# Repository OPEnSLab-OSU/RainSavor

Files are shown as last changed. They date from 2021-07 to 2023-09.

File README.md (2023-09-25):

# RainSavor
The RainSavor system by the OPEnS Lab measures the electrical conductivity of rainfall. Precipitation is collected in a cup with 2 wires for measuring electrical conductivity at the bottom and two wires for measuring water height at the top. The cup is emptied automatically from the bottom once the water reaches a set height by a siphon. The maximum measurable conductivity value and resolution are set with an I2C AD5246 variable resistor. Temperature and relative humidity are measured with an SHT31 sensor. All data is timestamped and logged to a microSD card at a set time interval with the device on standby between measurements. See the RainSavor wiki for more information: https://github.com/OPEnSLab-OSU/OPEnS-Lab-Home/wiki/RainSavor.

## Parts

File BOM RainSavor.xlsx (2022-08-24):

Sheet: Title Page and Total Cost
RainSavor Bill of Materials
Document updated/edited by: | Cameron Whitlow
Most recent update: | 2021-08-03
Per 1 Smart Rock:
Mechanical Components Total: | $106.55
Electrical Components Total: | $92.84
Labor:
Overall Cost: | $199.39

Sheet: Mechanical Components
Mechanical Components
Cost per device: | $106.55
ID number | Item Description | Quantity Given | Quantity per device | Retail Cost | Cost Per Device | Purchasing quantity | Cost for Required quantity | Product/site info | Notes
 | Davis Rain Funnel | 1 | 1 | $31.95 | $31.95 | 1 |  | Weathershack (https://www.weathershack.com/product/davis-instruments-6462.html)
 | Horizontal T Post | 4 | 1 | $19.29 | $4.82 |  |  | Amazon (https://www.amazon.com/T-Post-Bracket-3-Horizonta-4-Pack/dp/B01NB0FTKH)
 | Vertical T Post | 4 | 1 | $19.29 | $4.82 |  |  | Amazon (https://www.amazon.com/EFL-T-Post-Bracket-Vertical-4-Pack/dp/B01N17VLPI)
 | Pelican Case | 1 | 1 | $14.72 | $14.72 |  |  | BHphotovideo (https://www.bhphotovideo.com/c/product/257871-REG/Pelican_1040_025_120_1040_Micro_Case_Solid.html)
 | Tough Resin | 1 | 1 | $8.00 | $8.00
 | ASA for mount | 1 | 1 | $2.00 | $2.00
 | PG7 Cable Glands | 20 | 2 | $7.99 | $0.80 | 1 |  | Amazon (https://smile.amazon.com/Lokman-Plastic-Waterproof-Adjustable-Connectors/dp/B06Y5HGYK2)
 | Silica Packets |  | 1
 | Screws
 | Hex Nuts
 | T post | 1 | 1 | $3.99 | $3.99 | 1 |  | Tractor Supply (https://www.tractorsupply.com/tsc/product/studded-t-post-5-ft-125-lb-per-foot-3609099)
F221B1/16 BK100 | Heat Shrink | 1 | 1 | $16.00 | $16.00 |  |  | Digikey (https://www.digikey.com/en/products/detail/alpha-wire/F221B1-16-BK100/281667) | For waterproofing solder joint/protecting against shorts
PRT-11375 | Colored Wire | 1 | 1 | $16.95 | $16.95 |  |  | Digikey (https://www.digikey.com/en/products/detail/sparkfun-electronics/PRT-11375/5956252) | This is enough wire to make multiple units, other sources for smaller amounts can be found
744 | Waterproof Connector | 1 | 1 | $2.50 | $2.50 |  |  | Adafruit (https://www.adafruit.com/product/744) | Connection between pelican case and the davis rain funnel
 |  |  |  |  | #DIV/0!
 |  |  |  |  | #DIV/0!
 |  |  |  |  | #DIV/0!
 |  |  |  |  | #DIV/0!
 |  |  |  |  | #DIV/0!
 |  |  |  |  | #DIV/0!
 |  |  |  |  | #DIV/0!
 |  |  |  |  | #DIV/0!
 |  |  |  |  | #DIV/0!
 |  |  |  |  | #DIV/0!
 |  |  |  |  | #DIV/0!
 |  |  |  |  | #DIV/0!
 |  |  |  |  | #DIV/0!
 |  |  |  |  | #DIV/0!
 |  |  |  |  | #DIV/0!
 |  |  |  |  | #DIV/0!
 |  |  |  |  | #DIV/0!
 |  |  |  |  | #DIV/0!
 |  |  |  |  | #DIV/0!
 |  |  |  |  | #DIV/0!
 |  |  |  |  | #DIV/0!
 |  |  |  |  | #DIV/0!
 |  |  |  |  | #DIV/0!
 |  |  |  |  | #DIV/0!
 |  |  |  |  | #DIV/0!
 |  |  |  |  | #DIV/0!
 |  |  |  |  | #DIV/0!
 |  |  |  |  | #DIV/0!
 |  |  |  |  | #DIV/0!
 |  |  |  |  | #DIV/0!
 |  |  |  |  | #DIV/0!
 |  |  |  |  | #DIV/0!
 |  |  |  |  | #DIV/0!
 |  |  |  |  | #DIV/0!
 |  |  |  |  | #DIV/0!
 |  |  |  |  | #DIV/0!
 |  |  |  |  | #DIV/0!
 |  |  |  |  | #DIV/0!
 |  |  |  |  | #DIV/0!
 |  |  |  |  | #DIV/0!
 |  |  |  |  | #DIV/0!
 |  |  |  |  | $0.00
 |  |  |  |  | $0.00
 |  |  |  |  | $0.00
 |  |  |  |  | $0.00
 |  |  |  |  | $0.00
 |  |  |  |  | $0.00
 |  |  |  |  | $0.00
 |  |  |  |  | $0.00
 |  |  |  |  | $0.00
 |  |  |  |  | $0.00
 |  |  |  |  | $0.00
 |  |  |  |  | $0.00
 |  |  |  |  | $0.00
 |  |  |  |  | $0.00
 |  |  |  |  | $0.00
 |  |  |  |  | $0.00
 |  |  |  |  | $0.00
 |  |  |  |  | $0.00
 |  |  |  |  | $0.00
 |  |  |  |  | $0.00
 |  |  |  |  | $0.00
 |  |  |  |  | $0.00
 |  |  |  |  | $0.00
 |  |  |  |  | $0.00
 |  |  |  |  | $0.00
 |  |  |  |  | $0.00
 |  |  |  |  | $0.00
 |  |  |  |  | $0.00
 |  |  |  |  | $0.00
 |  |  |  |  | $0.00
 |  |  |  |  | $0.00
 |  |  |  |  | $0.00
 |  |  |  |  | $0.00
 |  |  |  |  | $0.00
 |  |  |  |  | $0.00
 |  |  |  |  | $0.00
 |  |  |  |  | $0.00
 |  |  |  |  | $0.00
 |  |  |  |  | $0.00
 |  |  |  |  | $0.00
 |  |  |  |  | $0.00
 |  |  |  |  | $0.00
 |  |  |  |  | $0.00
 |  |  |  |  | $0.00
 |  |  |  |  | $0.00
 |  |  |  |  | $0.00
 |  |  |  |  | $0.00
 |  |  |  |  | $0.00
 |  |  |  |  | $0.00
 |  |  |  |  | $0.00
 |  |  |  |  | $0.00
 |  |  |  |  | $0.00
 |  |  |  |  | $0.00
 |  |  |  |  | $0.00
 |  |  |  |  | $0.00
 |  |  |  |  | $0.00
 |  |  |  |  | $0.00
 |  |  |  |  | $0.00
 |  |  |  |  | $0.00
 |  |  |  |  | $0.00
 |  |  |  |  | $0.00
 |  |  |  |  | $0.00
 |  |  |  |  | $0.00
 |  |  |  |  | $0.00
 |  |  |  |  | $0.00
 |  |  |  |  | $0.00
 |  |  |  |  | $0.00
 |  |  |  |  | $0.00
 |  |  |  |  | $0.00
 |  |  |  |  | $0.00
 |  |  |  |  | $0.00
 |  |  |  |  | $0.00
 |  |  |  |  | $0.00
 |  |  |  |  | $0.00
 |  |  |  |  | $0.00
 |  |  |  |  | $0.00
 |  |  |  |  | $0.00
 |  |  |  |  | $0.00
 |  |  |  |  | $0.00
 |  |  |  |  | $0.00
 |  |  |  |  | $0.00
 |  |  |  |  | $0.00
 |  |  |  |  | $0.00
 |  |  |  |  | $0.00
 |  |  |  |  | $0.00
 |  |  |  |  | $0.00
 |  |  |  |  | $0.00
 |  |  |  |  | $0.00
 |  |  |  |  | $0.00
 |  |  |  |  | $0.00
 |  |  |  |  | $0.00
 |  |  |  |  | $0.00
 |  |  |  |  | $0.00
 |  |  |  |  | $0.00
 |  |  |  |  | $0.00
 |  |  |  |  | $0.00
 |  |  |  |  | $0.00
 |  |  |  |  | $0.00
 |  |  |  |  | $0.00
 |  |  |  |  | $0.00
 |  |  |  |  | $0.00
 |  |  |  |  | $0.00
 |  |  |  |  | $0.00
 |  |  |  |  | $0.00
 |  |  |  |  | $0.00
 |  |  |  |  | $0.00
 |  |  |  |  | $0.00
 |  |  |  |  | $0.00
 |  |  |  |  | $0.00
 |  |  |  |  | $0.00
 |  |  |  |  | $0.00
 |  |  |  |  | $0.00
 |  |  |  |  | $0.00
 |  |  |  |  | $0.00
 |  |  |  |  | $0.00
 |  |  |  |  | $0.00
 |  |  |  |  | $0.00
 |  |  |  |  | $0.00
 |  |  |  |  | $0.00
 |  |  |  |  | $0.00
 |  |  |  |  | $0.00
 |  |  |  |  | $0.00
 |  |  |  |  | $0.00
 |  |  |  |  | $0.00
 |  |  |  |  | $0.00
 |  |  |  |  | $0.00
 |  |  |  |  | $0.00
 |  |  |  |  | $0.00
 |  |  |  |  | $0.00
 |  |  |  |  | $0.00
 |  |  |  |  | $0.00
 |  |  |  |  | $0.00
 |  |  |  |  | $0.00
 |  |  |  |  | $0.00
 |  |  |  |  | $0.00
 |  |  |  |  | $0.00
 |  |  |  |  | $0.00
 |  |  |  |  | $0.00
 |  |  |  |  | $0.00
 |  |  |  |  | $0.00
 |  |  |  |  | $0.00
 |  |  |  |  | $0.00
 |  |  |  |  | $0.00
 |  |  |  |  | $0.00
 |  |  |  |  | $0.00
 |  |  |  |  | $0.00
 |  |  |  |  | $0.00
 |  |  |  |  | $0.00
 |  |  |  |  | $0.00
 |  |  |  |  | $0.00
 |  |  |  |  | $0.00
 |  |  |  |  | $0.00
 |  |  |  |  | $0.00
 |  |  |  |  | $0.00
 |  |  |  |  | $0.00
 |  |  |  |  | $0.00
 |  |  |  |  | $0.00
 |  |  |  |  | $0.00
 |  |  |  |  | $0.00
 |  |  |  |  | $0.00
 |  |  |  |  | $0.00
 |  |  |  |  | $0.00
 |  |  |  |  | $0.00
 |  |  |  |  | $0.00
 |  |  |  |  | $0.00
 |  |  |  |  | $0.00
 |  |  |  |  | $0.00
 |  |  |  |  | $0.00
 |  |  |  |  | $0.00
 |  |  |  |  | $0.00
 |  |  |  |  | $0.00
 |  |  |  |  | $0.00
 |  |  |  |  | $0.00
 |  |  |  |  | $0.00
 |  |  |  |  | $0.00
 |  |  |  |  | $0.00
 |  |  |  |  | $0.00
 |  |  |  |  | $0.00
 |  |  |  |  | $0.00
 |  |  |  |  | $0.00
 |  |  |  |  | $0.00
 |  |  |  |  | $0.00
 |  |  |  |  | $0.00
 |  |  |  |  | $0.00
 |  |  |  |  | $0.00
 |  |  |  |  | $0.00
 |  |  |  |  | $0.00
 |  |  |  |  | $0.00
 |  |  |  |  | $0.00
 |  |  |  |  | $0.00
 |  |  |  |  | $0.00
 |  |  |  |  | $0.00
 |  |  |  |  | $0.00
 |  |  |  |  | $0.00
 |  |  |  |  | $0.00
 |  |  |  |  | $0.00
 |  |  |  |  | $0.00
 |  |  |  |  | $0.00
 |  |  |  |  | $0.00
 |  |  |  |  | $0.00
 |  |  |  |  | $0.00
 |  |  |  |  | $0.00
 |  |  |  |  | $0.00
 |  |  |  |  | $0.00
 |  |  |  |  | $0.00
 |  |  |  |  | $0.00
 |  |  |  |  | $0.00
 |  |  |  |  | $0.00
 |  |  |  |  | $0.00
 |  |  |  |  | $0.00
 |  |  |  |  | $0.00
 |  |  |  |  | $0.00
 |  |  |  |  | $0.00
 |  |  |  |  | $0.00
 |  |  |  |  | $0.00
 |  |  |  |  | $0.00
 |  |  |  |  | $0.00
 |  |  |  |  | $0.00
 |  |  |  |  | $0.00
 |  |  |  |  | $0.00
 |  |  |  |  | $0.00
 |  |  |  |  | $0.00
 |  |  |  |  | $0.00
 |  |  |  |  | $0.00
 |  |  |  |  | $0.00
 |  |  |  |  | $0.00
 |  |  |  |  | $0.00
 |  |  |  |  | $0.00
 |  |  |  |  | $0.00
 |  |  |  |  | $0.00
 |  |  |  |  | $0.00
 |  |  |  |  | $0.00
 |  |  |  |  | $0.00
 |  |  |  |  | $0.00
 |  |  |  |  | $0.00
 |  |  |  |  | $0.00
 |  |  |  |  | $0.00
 |  |  |  |  | $0.00
 |  |  |  |  | $0.00
 |  |  |  |  | $0.00
 |  |  |  |  | $0.00
 |  |  |  |  | $0.00
 |  |  |  |  | $0.00
 |  |  |  |  | $0.00
 |  |  |  |  | $0.00
 |  |  |  |  | $0.00
 |  |  |  |  | $0.00
 |  |  |  |  | $0.00
 |  |  |  |  | $0.00
 |  |  |  |  | $0.00
 |  |  |  |  | $0.00
 |  |  |  |  | $0.00
 |  |  |  |  | $0.00
 |  |  |  |  | $0.00
 |  |  |  |  | $0.00
 |  |  |  |  | $0.00
 |  |  |  |  | $0.00
 |  |  |  |  | $0.00
 |  |  |  |  | $0.00
 |  |  |  |  | $0.00
 |  |  |  |  | $0.00
 |  |  |  |  | $0.00
 |  |  |  |  | $0.00
 |  |  |  |  | $0.00
 |  |  |  |  | $0.00
 |  |  |  |  | $0.00
 |  |  |  |  | $0.00
 |  |  |  |  | $0.00
 |  |  |  |  | $0.00
 |  |  |  |  | $0.00
 |  |  |  |  | $0.00
 |  |  |  |  | $0.00
 |  |  |  |  | $0.00
 |  |  |  |  | $0.00
 |  |  |  |  | $0.00
 |  |  |  |  | $0.00
 |  |  |  |  | $0.00
 |  |  |  |  | $0.00
 |  |  |  |  | $0.00
 |  |  |  |  | $0.00
 |  |  |  |  | $0.00
 |  |  |  |  | $0.00
 |  |  |  |  | $0.00
 |  |  |  |  | $0.00
 |  |  |  |  | $0.00
 |  |  |  |  | $0.00
 |  |  |  |  | $0.00
 |  |  |  |  | $0.00
 |  |  |  |  | $0.00
 |  |  |  |  | $0.00
 |  |  |  |  | $0.00
 |  |  |  |  | $0.00
 |  |  |  |  | $0.00
 |  |  |  |  | $0.00
 |  |  |  |  | $0.00
 |  |  |  |  | $0.00
 |  |  |  |  | $0.00
 |  |  |  |  | $0.00
 |  |  |  |  | $0.00
 |  |  |  |  | $0.00
 |  |  |  |  | $0.00
 |  |  |  |  | $0.00
 |  |  |  |  | $0.00
 |  |  |  |  | $0.00
 |  |  |  |  | $0.00
 |  |  |  |  | $0.00
 |  |  |  |  | $0.00
 |  |  |  |  | $0.00
 |  |  |  |  | $0.00
 |  |  |  |  | $0.00
 |  |  |  |  | $0.00
 |  |  |  |  | $0.00
 |  |  |  |  | $0.00
 |  |  |  |  | $0.00
 |  |  |  |  | $0.00
 |  |  |  |  | $0.00
 |  |  |  |  | $0.00
 |  |  |  |  | $0.00
 |  |  |  |  | $0.00
 |  |  |  |  | $0.00
 |  |  |  |  | $0.00
 |  |  |  |  | $0.00
 |  |  |  |  | $0.00
 |  |  |  |  | $0.00
 |  |  |  |  | $0.00
 |  |  |  |  | $0.00
 |  |  |  |  | $0.00
 |  |  |  |  | $0.00
 |  |  |  |  | $0.00
 |  |  |  |  | $0.00
 |  |  |  |  | $0.00
 |  |  |  |  | $0.00
 |  |  |  |  | $0.00
 |  |  |  |  | $0.00
 |  |  |  |  | $0.00
 |  |  |  |  | $0.00
 |  |  |  |  | $0.00
 |  |  |  |  | $0.00
 |  |  |  |  | $0.00
 |  |  |  |  | $0.00
 |  |  |  |  | $0.00
 |  |  |  |  | $0.00
 |  |  |  |  | $0.00
 |  |  |  |  | $0.00
 |  |  |  |  | $0.00
 |  |  |  |  | $0.00
 |  |  |  |  | $0.00
 |  |  |  |  | $0.00
 |  |  |  |  | $0.00
 |  |  |  |  | $0.00
 |  |  |  |  | $0.00
 |  |  |  |  | $0.00
 |  |  |  |  | $0.00
 |  |  |  |  | $0.00
 |  |  |  |  | $0.00
 |  |  |  |  | $0.00
 |  |  |  |  | $0.00
 |  |  |  |  | $0.00
 |  |  |  |  | $0.00
 |  |  |  |  | $0.00
 |  |  |  |  | $0.00
 |  |  |  |  | $0.00
 |  |  |  |  | $0.00
 |  |  |  |  | $0.00
 |  |  |  |  | $0.00
 |  |  |  |  | $0.00
 |  |  |  |  | $0.00
 |  |  |  |  | $0.00
 |  |  |  |  | $0.00
 |  |  |  |  | $0.00
 |  |  |  |  | $0.00
 |  |  |  |  | $0.00
 |  |  |  |  | $0.00
 |  |  |  |  | $0.00
 |  |  |  |  | $0.00
 |  |  |  |  | $0.00
 |  |  |  |  | $0.00
 |  |  |  |  | $0.00
 |  |  |  |  | $0.00
 |  |  |  |  | $0.00
 |  |  |  |  | $0.00
 |  |  |  |  | $0.00
 |  |  |  |  | $0.00
 |  |  |  |  | $0.00
 |  |  |  |  | $0.00
 |  |  |  |  | $0.00
 |  |  |  |  | $0.00
 |  |  |  |  | $0.00
 |  |  |  |  | $0.00
 |  |  |  |  | $0.00
 |  |  |  |  | $0.00
 |  |  |  |  | $0.00
 |  |  |  |  | $0.00
 |  |  |  |  | $0.00
 |  |  |  |  | $0.00
 |  |  |  |  | $0.00
 |  |  |  |  | $0.00
 |  |  |  |  | $0.00
 |  |  |  |  | $0.00
 |  |  |  |  | $0.00
 |  |  |  |  | $0.00
 |  |  |  |  | $0.00
 |  |  |  |  | $0.00
 |  |  |  |  | $0.00
 |  |  |  |  | $0.00
 |  |  |  |  | $0.00
 |  |  |  |  | $0.00
 |  |  |  |  | $0.00
 |  |  |  |  | $0.00
 |  |  |  |  | $0.00
 |  |  |  |  | $0.00
 |  |  |  |  | $0.00
 |  |  |  |  | $0.00
 |  |  |  |  | $0.00
 |  |  |  |  | $0.00
 |  |  |  |  | $0.00
 |  |  |  |  | $0.00
 |  |  |  |  | $0.00
 |  |  |  |  | $0.00
 |  |  |  |  | $0.00
 |  |  |  |  | $0.00
 |  |  |  |  | $0.00
 |  |  |  |  | $0.00
 |  |  |  |  | $0.00
 |  |  |  |  | $0.00
 |  |  |  |  | $0.00
 |  |  |  |  | $0.00
 |  |  |  |  | $0.00
 |  |  |  |  | $0.00
 |  |  |  |  | $0.00
 |  |  |  |  | $0.00
 |  |  |  |  | $0.00
 |  |  |  |  | $0.00
 |  |  |  |  | $0.00
 |  |  |  |  | $0.00
 |  |  |  |  | $0.00
 |  |  |  |  | $0.00
 |  |  |  |  | $0.00
 |  |  |  |  | $0.00
 |  |  |  |  | $0.00
 |  |  |  |  | $0.00
 |  |  |  |  | $0.00
 |  |  |  |  | $0.00
 |  |  |  |  | $0.00
 |  |  |  |  | $0.00
 |  |  |  |  | $0.00
 |  |  |  |  | $0.00
 |  |  |  |  | $0.00
 |  |  |  |  | $0.00
 |  |  |  |  | $0.00
 |  |  |  |  | $0.00
 |  |  |  |  | $0.00
 |  |  |  |  | $0.00
 |  |  |  |  | $0.00
 |  |  |  |  | $0.00
 |  |  |  |  | $0.00
 |  |  |  |  | $0.00
 |  |  |  |  | $0.00
 |  |  |  |  | $0.00
 |  |  |  |  | $0.00
 |  |  |  |  | $0.00
 |  |  |  |  | $0.00
 |  |  |  |  | $0.00
 |  |  |  |  | $0.00
 |  |  |  |  | $0.00
 |  |  |  |  | $0.00
 |  |  |  |  | $0.00
 |  |  |  |  | $0.00
 |  |  |  |  | $0.00
 |  |  |  |  | $0.00
 |  |  |  |  | $0.00
 |  |  |  |  | $0.00
 |  |  |  |  | $0.00
 |  |  |  |  | $0.00
 |  |  |  |  | $0.00
 |  |  |  |  | $0.00
 |  |  |  |  | $0.00
 |  |  |  |  | $0.00
 |  |  |  |  | $0.00
 |  |  |  |  | $0.00
 |  |  |  |  | $0.00
 |  |  |  |  | $0.00
 |  |  |  |  | $0.00
 |  |  |  |  | $0.00
 |  |  |  |  | $0.00
 |  |  |  |  | $0.00
 |  |  |  |  | $0.00
 |  |  |  |  | $0.00
 |  |  |  |  | $0.00
 |  |  |  |  | $0.00
 |  |  |  |  | $0.00
 |  |  |  |  | $0.00
 |  |  |  |  | $0.00
 |  |  |  |  | $0.00
 |  |  |  |  | $0.00
 |  |  |  |  | $0.00
 |  |  |  |  | $0.00
 |  |  |  |  | $0.00
 |  |  |  |  | $0.00
 |  |  |  |  | $0.00
 |  |  |  |  | $0.00
 |  |  |  |  | $0.00
 |  |  |  |  | $0.00
 |  |  |  |  | $0.00
 |  |  |  |  | $0.00
 |  |  |  |  | $0.00
 |  |  |  |  | $0.00
 |  |  |  |  | $0.00
 |  |  |  |  | $0.00
 |  |  |  |  | $0.00
 |  |  |  |  | $0.00
 |  |  |  |  | $0.00
 |  |  |  |  | $0.00
 |  |  |  |  | $0.00
 |  |  |  |  | $0.00
 |  |  |  |  | $0.00
 |  |  |  |  | $0.00
 |  |  |  |  | $0.00
 |  |  |  |  | $0.00
 |  |  |  |  | $0.00
 |  |  |  |  | $0.00
 |  |  |  |  | $0.00
 |  |  |  |  | $0.00
 |  |  |  |  | $0.00
 |  |  |  |  | $0.00
 |  |  |  |  | $0.00
 |  |  |  |  | $0.00
 |  |  |  |  | $0.00
 |  |  |  |  | $0.00
 |  |  |  |  | $0.00
 |  |  |  |  | $0.00
 |  |  |  |  | $0.00
 |  |  |  |  | $0.00
 |  |  |  |  | $0.00
 |  |  |  |  | $0.00
 |  |  |  |  | $0.00
 |  |  |  |  | $0.00
 |  |  |  |  | $0.00
 |  |  |  |  | $0.00
 |  |  |  |  | $0.00
 |  |  |  |  | $0.00
 |  |  |  |  | $0.00
 |  |  |  |  | $0.00
 |  |  |  |  | $0.00
 |  |  |  |  | $0.00
 |  |  |  |  | $0.00
 |  |  |  |  | $0.00
 |  |  |  |  | $0.00
 |  |  |  |  | $0.00
 |  |  |  |  | $0.00
 |  |  |  |  | $0.00
 |  |  |  |  | $0.00
 |  |  |  |  | $0.00
 |  |  |  |  | $0.00
 |  |  |  |  | $0.00
 |  |  |  |  | $0.00
 |  |  |  |  | $0.00
 |  |  |  |  | $0.00
 |  |  |  |  | $0.00
 |  |  |  |  | $0.00
 |  |  |  |  | $0.00
 |  |  |  |  | $0.00
 |  |  |  |  | $0.00
 |  |  |  |  | $0.00
 |  |  |  |  | $0.00
 |  |  |  |  | $0.00
 |  |  |  |  | $0.00
 |  |  |  |  | $0.00
 |  |  |  |  | $0.00
 |  |  |  |  | $0.00
 |  |  |  |  | $0.00
 |  |  |  |  | $0.00
 |  |  |  |  | $0.00
 |  |  |  |  | $0.00
 |  |  |  |  | $0.00
 |  |  |  |  | $0.00
 |  |  |  |  | $0.00
 |  |  |  |  | $0.00
 |  |  |  |  | $0.00
 |  |  |  |  | $0.00
 |  |  |  |  | $0.00
 |  |  |  |  | $0.00
 |  |  |  |  | $0.00
 |  |  |  |  | $0.00
 |  |  |  |  | $0.00
 |  |  |  |  | $0.00
 |  |  |  |  | $0.00
 |  |  |  |  | $0.00
 |  |  |  |  | $0.00
 |  |  |  |  | $0.00
 |  |  |  |  | $0.00
 |  |  |  |  | $0.00
 |  |  |  |  | $0.00
 |  |  |  |  | $0.00
 |  |  |  |  | $0.00
 |  |  |  |  | $0.00
 |  |  |  |  | $0.00
 |  |  |  |  | $0.00
 |  |  |  |  | $0.00
 |  |  |  |  | $0.00
 |  |  |  |  | $0.00
 |  |  |  |  | $0.00
 |  |  |  |  | $0.00
 |  |  |  |  | $0.00
 |  |  |  |  | $0.00
 |  |  |  |  | $0.00
 |  |  |  |  | $0.00
 |  |  |  |  | $0.00
 |  |  |  |  | $0.00
 |  |  |  |  | $0.00
 |  |  |  |  | $0.00
 |  |  |  |  | $0.00
 |  |  |  |  | $0.00
 |  |  |  |  | $0.00
 |  |  |  |  | $0.00
 |  |  |  |  | $0.00
 |  |  |  |  | $0.00
 |  |  |  |  | $0.00
 |  |  |  |  | $0.00
 |  |  |  |  | $0.00
 |  |  |  |  | $0.00
 |  |  |  |  | $0.00
 |  |  |  |  | $0.00
 |  |  |  |  | $0.00
 |  |  |  |  | $0.00
 |  |  |  |  | $0.00
 |  |  |  |  | $0.00
 |  |  |  |  | $0.00
 |  |  |  |  | $0.00
 |  |  |  |  | $0.00
 |  |  |  |  | $0.00
 |  |  |  |  | $0.00
 |  |  |  |  | $0.00
 |  |  |  |  | $0.00
 |  |  |  |  | $0.00
 |  |  |  |  | $0.00
 |  |  |  |  | $0.00
 |  |  |  |  | $0.00
 |  |  |  |  | $0.00
 |  |  |  |  | $0.00
 |  |  |  |  | $0.00
 |  |  |  |  | $0.00
 |  |  |  |  | $0.00
 |  |  |  |  | $0.00
 |  |  |  |  | $0.00
 |  |  |  |  | $0.00
 |  |  |  |  | $0.00
 |  |  |  |  | $0.00
 |  |  |  |  | $0.00
 |  |  |  |  | $0.00
 |  |  |  |  | $0.00
 |  |  |  |  | $0.00
 |  |  |  |  | $0.00
 |  |  |  |  | $0.00
 |  |  |  |  | $0.00
 |  |  |  |  | $0.00
 |  |  |  |  | $0.00
 |  |  |  |  | $0.00
 |  |  |  |  | $0.00
 |  |  |  |  | $0.00
 |  |  |  |  | $0.00
 |  |  |  |  | $0.00
 |  |  |  |  | $0.00
 |  |  |  |  | $0.00
 |  |  |  |  | $0.00
 |  |  |  |  | $0.00
 |  |  |  |  | $0.00
 |  |  |  |  | $0.00
 |  |  |  |  | $0.00
 |  |  |  |  | $0.00
 |  |  |  |  | $0.00
 |  |  |  |  | $0.00
 |  |  |  |  | $0.00
 |  |  |  |  | $0.00
 |  |  |  |  | $0.00
 |  |  |  |  | $0.00
 |  |  |  |  | $0.00
 |  |  |  |  | $0.00
 |  |  |  |  | $0.00
 |  |  |  |  | $0.00
 |  |  |  |  | $0.00
 |  |  |  |  | $0.00
 |  |  |  |  | $0.00
 |  |  |  |  | $0.00
 |  |  |  |  | $0.00
 |  |  |  |  | $0.00
 |  |  |  |  | $0.00
 |  |  |  |  | $0.00
 |  |  |  |  | $0.00
 |  |  |  |  | $0.00
 |  |  |  |  | $0.00
 |  |  |  |  | $0.00
 |  |  |  |  | $0.00
 |  |  |  |  | $0.00
 |  |  |  |  | $0.00
 |  |  |  |  | $0.00
 |  |  |  |  | $0.00
 |  |  |  |  | $0.00
 |  |  |  |  | $0.00
 |  |  |  |  | $0.00
 |  |  |  |  | $0.00
 |  |  |  |  | $0.00
 |  |  |  |  | $0.00
 |  |  |  |  | $0.00
 |  |  |  |  | $0.00
 |  |  |  |  | $0.00
 |  |  |  |  | $0.00
 |  |  |  |  | $0.00
 |  |  |  |  | $0.00
 |  |  |  |  | $0.00
 |  |  |  |  | $0.00
 |  |  |  |  | $0.00
 |  |  |  |  | $0.00
 |  |  |  |  | $0.00
 |  |  |  |  | $0.00
 |  |  |  |  | $0.00
 |  |  |  |  | $0.00
 |  |  |  |  | $0.00
 |  |  |  |  | $0.00
 |  |  |  |  | $0.00
 |  |  |  |  | $0.00
 |  |  |  |  | $0.00
 |  |  |  |  | $0.00
 |  |  |  |  | $0.00
 |  |  |  |  | $0.00
 |  |  |  |  | $0.00
 |  |  |  |  | $0.00
 |  |  |  |  | $0.00
 |  |  |  |  | $0.00
 |  |  |  |  | $0.00
 |  |  |  |  | $0.00
 |  |  |  |  | $0.00
 |  |  |  |  | $0.00
 |  |  |  |  | $0.00
 |  |  |  |  | $0.00
 |  |  |  |  | $0.00
 |  |  |  |  | $0.00
 |  |  |  |  | $0.00
 |  |  |  |  | $0.00
 |  |  |  |  | $0.00
 |  |  |  |  | $0.00
 |  |  |  |  | $0.00
 |  |  |  |  | $0.00
 |  |  |  |  | $0.00
 |  |  |  |  | $0.00
 |  |  |  |  | $0.00
 |  |  |  |  | $0.00
 |  |  |  |  | $0.00
 |  |  |  |  | $0.00
 |  |  |  |  | $0.00
 |  |  |  |  | $0.00
 |  |  |  |  | $0.00
 |  |  |  |  | $0.00
 |  |  |  |  | $0.00
 |  |  |  |  | $0.00
 |  |  |  |  | $0.00
 |  |  |  |  | $0.00
 |  |  |  |  | $0.00
 |  |  |  |  | $0.00
 |  |  |  |  | $0.00
 |  |  |  |  | $0.00
 |  |  |  |  | $0.00
 |  |  |  |  | $0.00
 |  |  |  |  | $0.00
 |  |  |  |  | $0.00
 |  |  |  |  | $0.00
 |  |  |  |  | $0.00
 |  |  |  |  | $0.00
 |  |  |  |  | $0.00
 |  |  |  |  | $0.00
 |  |  |  |  | $0.00
 |  |  |  |  | $0.00
 |  |  |  |  | $0.00
 |  |  |  |  | $0.00
 |  |  |  |  | $0.00
 |  |  |  |  | $0.00
 |  |  |  |  | $0.00
 |  |  |  |  | $0.00
 |  |  |  |  | $0.00
 |  |  |  |  | $0.00
 |  |  |  |  | $0.00
 |  |  |  |  | $0.00
 |  |  |  |  | $0.00
 |  |  |  |  | $0.00
 |  |  |  |  | $0.00
 |  |  |  |  | $0.00
 |  |  |  |  | $0.00
 |  |  |  |  | $0.00
 |  |  |  |  | $0.00
 |  |  |  |  | $0.00
 |  |  |  |  | $0.00
 |  |  |  |  | $0.00
 |  |  |  |  | $0.00
 |  |  |  |  | $0.00
 |  |  |  |  | $0.00
 |  |  |  |  | $0.00
 |  |  |  |  | $0.00
 |  |  |  |  | $0.00
 |  |  |  |  | $0.00
 |  |  |  |  | $0.00
 |  |  |  |  | $0.00
 |  |  |  |  | $0.00
 |  |  |  |  | $0.00
 |  |  |  |  | $0.00
 |  |  |  |  | $0.00
 |  |  |  |  | $0.00
 |  |  |  |  | $0.00
 |  |  |  |  | $0.00
 |  |  |  |  | $0.00
 |  |  |  |  | $0.00
 |  |  |  |  | $0.00
 |  |  |  |  | $0.00
 |  |  |  |  | $0.00
 |  |  |  |  | $0.00
 |  |  |  |  | $0.00
 |  |  |  |  | $0.00
 |  |  |  |  | $0.00
 |  |  |  |  | $0.00
 |  |  |  |  | $0.00
 |  |  |  |  | $0.00
 |  |  |  |  | $0.00
 |  |  |  |  | $0.00
 |  |  |  |  | $0.00
 |  |  |  |  | $0.00
 |  |  |  |  | $0.00
 |  |  |  |  | $0.00
 |  |  |  |  | $0.00
 |  |  |  |  | $0.00
 |  |  |  |  | $0.00
 |  |  |  |  | $0.00
 |  |  |  |  | $0.00
 |  |  |  |  | $0.00
 |  |  |  |  | $0.00
 |  |  |  |  | $0.00
 |  |  |  |  | $0.00
 |  |  |  |  | $0.00
 |  |  |  |  | $0.00
 |  |  |  |  | $0.00
 |  |  |  |  | $0.00
 |  |  |  |  | $0.00
 |  |  |  |  | $0.00
 |  |  |  |  | $0.00
 |  |  |  |  | $0.00
 |  |  |  |  | $0.00
 |  |  |  |  | $0.00
 |  |  |  |  | $0.00
 |  |  |  |  | $0.00
 |  |  |  |  | $0.00
 |  |  |  |  | $0.00
 |  |  |  |  | $0.00
 |  |  |  |  | $0.00
 |  |  |  |  | $0.00
 |  |  |  |  | $0.00
 |  |  |  |  | $0.00
 |  |  |  |  | $0.00
 |  |  |  |  | $0.00
 |  |  |  |  | $0.00
 |  |  |  |  | $0.00
 |  |  |  |  | $0.00
 |  |  |  |  | $0.00
 |  |  |  |  | $0.00
 |  |  |  |  | $0.00
 |  |  |  |  | $0.00
 |  |  |  |  | $0.00
 |  |  |  |  | $0.00
 |  |  |  |  | $0.00
 |  |  |  |  | $0.00
 |  |  |  |  | $0.00
 |  |  |  |  | $0.00
 |  |  |  |  | $0.00
 |  |  |  |  | $0.00
 |  |  |  |  | $0.00
 |  |  |  |  | $0.00
 |  |  |  |  | $0.00
 |  |  |  |  | $0.00
 |  |  |  |  | $0.00
 |  |  |  |  | $0.00
 |  |  |  |  | $0.00
 |  |  |  |  | $0.00
 |  |  |  |  | $0.00
 |  |  |  |  | $0.00
 |  |  |  |  | $0.00
 |  |  |  |  | $0.00
 |  |  |  |  | $0.00
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

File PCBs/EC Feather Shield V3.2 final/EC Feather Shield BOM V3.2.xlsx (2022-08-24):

Item # | Comp # | Qty | Manufacturer | Mfg Part # | Description/Value | Package, Case | Type | Cost per Part | Total Cost
1 | U1 | 1 | Digikey (https://www.digikey.com/en/products/detail/texas-instruments/ADS1115IDGST/2123298) | 296-24934-1-ND | IC ADC 16BIT SIGMA-DELTA 10VSSOP | 10-TFSOP, 10-MSOP (0.118", 3.00mm Width) | Surface Mount | $6.10 | $6.10
2 | U2 | 1 | Digikey (https://www.digikey.com/en/products/detail/texas-instruments/TPS60400DBVR/1672052) | 296-27004-1-ND | IC REG CHARG PUMP INV 60MA SOT23 | SOT-23-5 | Surface Mount | $0.93 | $0.93
3 | U3 | 1 | Digikey (https://www.digikey.com/en/products/detail/texas-instruments/TL074CN/277423) | 296-1777-ND | IC OPAMP JFET 4 CIRCUIT 14DIP | 14-DIP | Through Hole | $0.65 | $0.65
4 | U4 | 1 | Digikey (https://www.digikey.com/en/products/detail/analog-devices-inc/AD5246BKSZ10-RL7/995693) | AD5246BKSZ10-RL7CT-ND | IC DGTL POT 10KOHM 128TAP SC70-6 | 6-TSSOP, SC-88, SOT-363 | Surface Mount | $1.52 | $1.52
5 | C1, C2, C3 | 3 | Digikey (https://www.digikey.com/en/products/detail/kemet/C1206C104KARACTU/992199) | 399-4674-1-ND | CAP CER 0.1UF 250V X7R 1206 | 1206 (3216 Metric) | Surface Mount | $0.35 | $1.05
6 | C4, C5, C6, C7, C8, C9, C10 | 7 | Digikey (https://www.digikey.com/en/products/detail/samsung-electro-mechanics/CL31B105KBHNFNE/3888749) | 1276-3091-1-ND | CAP CER 1UF 50V X7R 1206 | 1206 (3216 Metric) | Surface Mount | $0.15 | $1.05
7 | R1, R4, R6 | 3 | Digikey (https://www.digikey.com/en/products/detail/yageo/RC1206FR-071KL/728387) | 311-1.00KFRCT-ND | RES SMD 1K OHM 1% 1/4W 1206 | 1206 (3216 Metric) | Surface Mount | $0.10 | $0.30
8 | R5 | 1 | Digikey (https://www.digikey.com/en/products/detail/yageo/RC1206JR-072KL/732183) | 311-2.0KERCT-ND | RES SMD 2K OHM 5% 1/4W 1206 | 1206 (3216 Metric) | Surface Mount | $0.10 | $0.10
9 | R8, R11 | 2 | Digikey (https://www.digikey.com/en/products/detail/yageo/RC1206FR-074K7L/731834) | 311-4.70KFRCT-ND | RES SMD 4.7K OHM 1% 1/4W 1206 | 1206 (3216 Metric) | Surface Mount | $0.10 | $0.20
10 | R10 | 1 | Digikey (https://www.digikey.com/en/products/detail/yageo/RT1206BRD075KL/5936961) | YAG5090CT-ND | RES SMD 5K OHM 0.1% 1/4W 1206 | 1206 (3216 Metric) | Surface Mount | $0.63 | $0.63
11 | R2, R7, R9, R12, R13, R14, R15,R17,R18,R19 | 10 | Digikey (https://www.digikey.com/en/products/detail/yageo/RC1206JR-0710KL/732156) | 311-10KERCT-ND | RES SMD 10K OHM 5% 1/4W 1206 | 1206 (3216 Metric) | Surface Mount | $0.10 | $1.00
12 | R3 | 1 | Digikey (https://www.digikey.com/en/products/detail/yageo/RC1206JR-0722KL/732201) | 311-22KERCT-ND | RES SMD 22K OHM 5% 1/4W 1206 | 1206 (3216 Metric) | Surface Mount | $0.10 | $0.10
13 | D1, D2, D3, D4, D5 | 5 | Digikey (https://www.digikey.com/en/products/detail/comchip-technology/1N4001-G/1979675) | 641-1310-1-ND | DIODE GEN PURP 50V 1A DO41 | DO-204AL, DO-41, Axial | Through Hole | $0.10 | $0.50
14 | REED | 1 | Digikey (https://www.digikey.com/en/products/detail/e-switch/EG1218/101726) | EG1903-ND | SWITCH SLIDE SPDT 200MA 30V |  | Through Hole | $0.65 | $0.65
15 | CN1, CN4 | 2 | Digikey (https://www.digikey.com/en/products/detail/jst-sales-america-inc/B2B-PH-K-S(LF)(SN)/926611) | 455-1704-ND | CONN HEADER VERT 2POS 2MM |  | Through Hole | $0.17 | $0.34
16 | JP2 & JP3 (combo) | 1 | Digikey (https://www.digikey.com/en/products/detail/sullins-connector-solutions/PPTC161LFBN-RC/810154) | S7014-ND | CONN HDR 16POS 0.1 TIN PCB |  | Through Hole | $0.98 | $0.98
17 | JP1 | 1 | Digikey (https://www.digikey.com/en/products/detail/sullins-connector-solutions/PPTC121LFBN-RC/807231) | S6100-ND | CONN HDR 12POS 0.1 TIN PCB |  | Through Hole | $0.78 | $0.78
18 | JP5 | 1 | Digikey (https://www.digikey.com/en/products/detail/w%C3%BCrth-elektronik/61300311121/4846825) | 732-5316-ND | CONN HEADER VERT 3POS 2.54MM |  | Through Hole | $0.13 | $0.13
19 | PCB | 1 | OSHPark |  | PCB Print - 3 |  |  | $14.95 | $14.95 | Can also source PCB & Stencil through PCBWay
20 | PCB Stencil | 1 | OSHStencil |  | PCB Stencil |  |  | $22.22 | $22.22
21 | LED1, LED2, LED3 | 3 | Digikey (https://www.digikey.com/en/products/detail/kingbright/APTR3216SGC/1747570) | 754-1171-1-ND | LED GREEN CLEAR SMD BOTTOM ENTRY | 1206 (3216 Metric) | Surface Mount | $0.32 | $0.96
22 | JP4 | 1 | Digikey (https://www.digikey.com/en/products/detail/sullins-connector-solutions/PPPC091LFBN-RC/810181) | S7042-ND | CONN HDR 9POS 0.1 GOLD PCB |  | Through Hole | $0.67 | $0.67
23 | CN2 | 1 | Digikey (https://www.digikey.com/en/products/detail/jst-sales-america-inc/B3B-PH-K-S-LF-SN/926612) | 455-1705-ND | CONN HEADER VERT 3POS 2MM |  | Through Hole | $0.19 | $0.19
24 | CN3 | 1 | Digikey (https://www.digikey.com/en/products/detail/jst-sales-america-inc/B4B-PH-K-S-LF-SN/926613) | 455-1706-ND | CONN HEADER VERT 4POS 2MM |  | Through Hole | $0.24 | $0.24
25 | CN1-F, CN4-F | 2 | Digikey (https://www.digikey.com/en/products/detail/jst-sales-america-inc/PHR-2/608607?ColumnSort=0&FV=-8%7C319&page=1&pageSize=500&sf=0&sv=0) | 455-1165-ND | CONN HOUSING PH 2POS 2MM WHITE |  | Through Hole | $0.10 | $0.20
26 | CN2-F | 1 | Digikey (https://www.digikey.com/en/products/detail/jst-sales-america-inc/PHR-3/527357?ColumnSort=0&FV=-8%7C319&page=1&pageSize=500&sf=0&sv=0) | 455-1126-ND | CONN HOUSING PH 3POS 2.0MM |  | Through Hole | $0.10 | $0.10
27 | CN3-F | 1 | Digikey (https://www.digikey.com/en/products/detail/jst-sales-america-inc/PHR-4/608606?ColumnSort=0&FV=-8%7C319&page=1&pageSize=500&sf=0&sv=0) | 455-1164-ND | CONN HOUSING PH 4POS 2MM WHITE |  | Through Hole | $0.10 | $0.10
 |  |  |  |  |  |  | TOTAL | $51.80 | $55.81
 | Alternatives for U4
1 | U4-2 | 1 | Digikey (https://www.digikey.com/en/products/detail/analog-devices-inc/AD5246BKSZ50-RL7/995689) | AD5246BKSZ50-RL7CT-ND | IC DGTL POT 50KOHM 128TAP SC70-6 | 6-TSSOP, SC-88, SOT-363 | Surface Mount | $1.52
2 | U4-3 | 1 | Digikey (https://www.digikey.com/en/products/detail/analog-devices-inc/AD5246BKSZ100-RL7/750896) | AD5246BKSZ100RLCT-ND | IC DGT POT 100KOHM 128TAP SC70-6 | 6-TSSOP, SC-88, SOT-363 | Surface Mount | $1.52

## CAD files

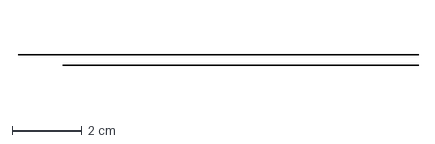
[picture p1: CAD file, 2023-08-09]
CAD/3L_bag_holder.dxf
11.5 x 0.3 cm

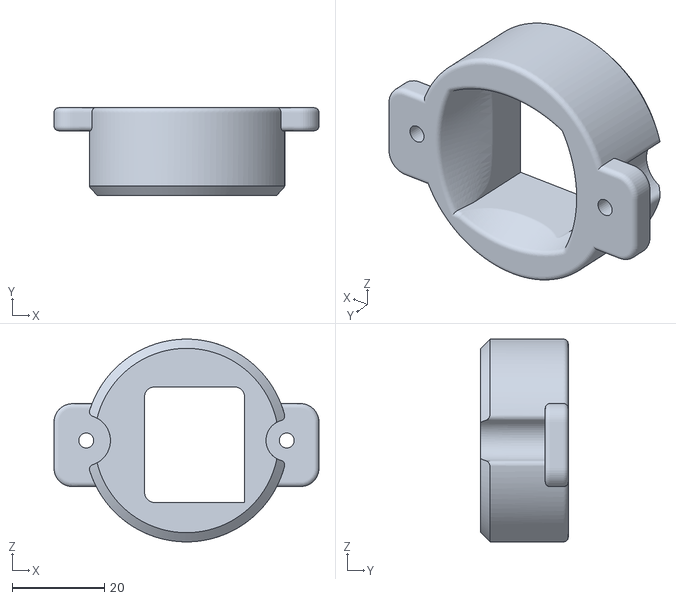
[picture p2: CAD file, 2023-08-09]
CAD/RainSavor_Sleeve.stl
57.5 x 19.0 x 44.0

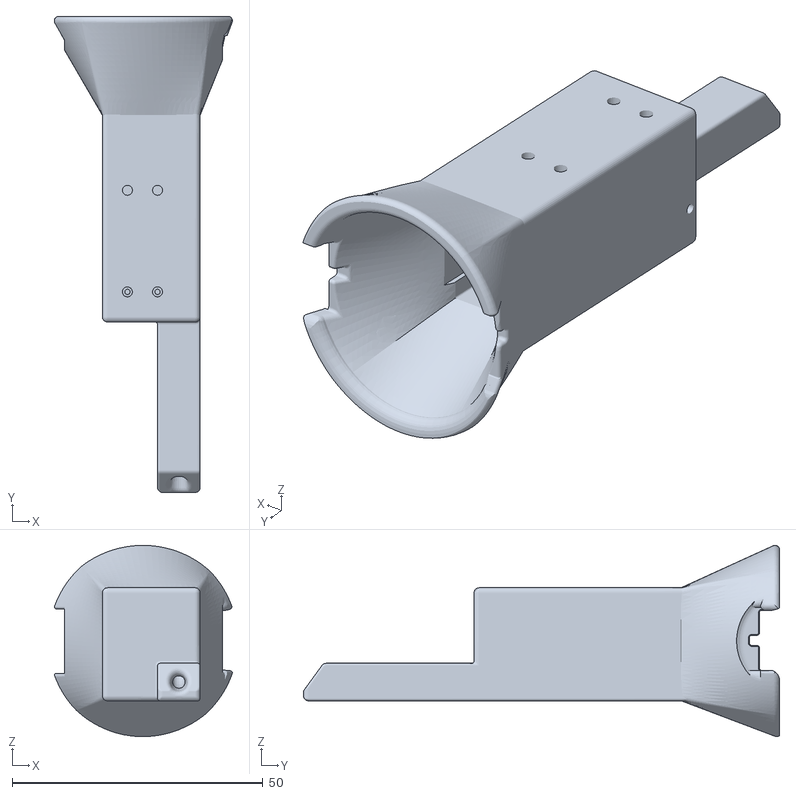
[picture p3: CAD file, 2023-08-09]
CAD/RainSavor_Cup_Funnel.stl
35.6 x 94.9 x 38.1

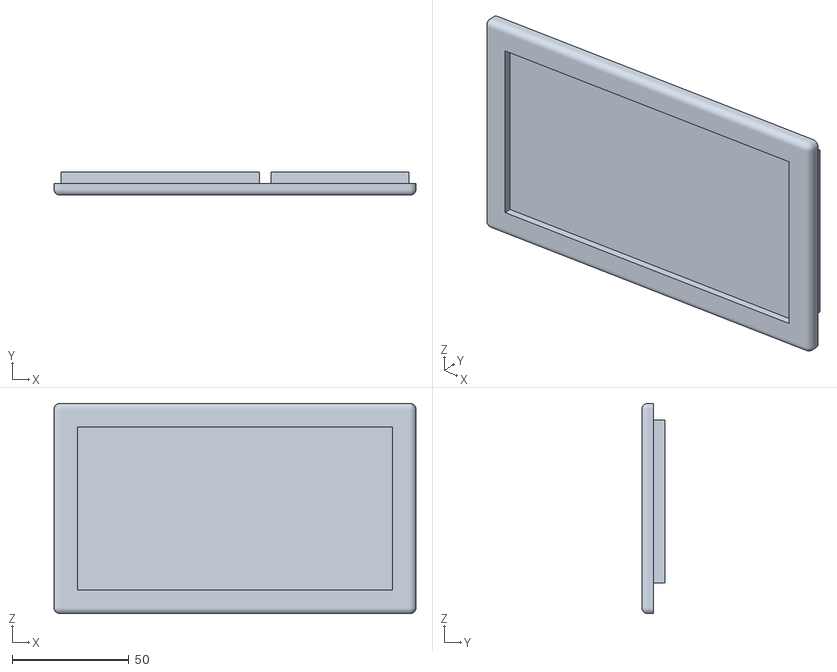
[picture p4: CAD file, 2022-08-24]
CAD/PCB_battery_mount.stl
155.0 x 10.0 x 90.0

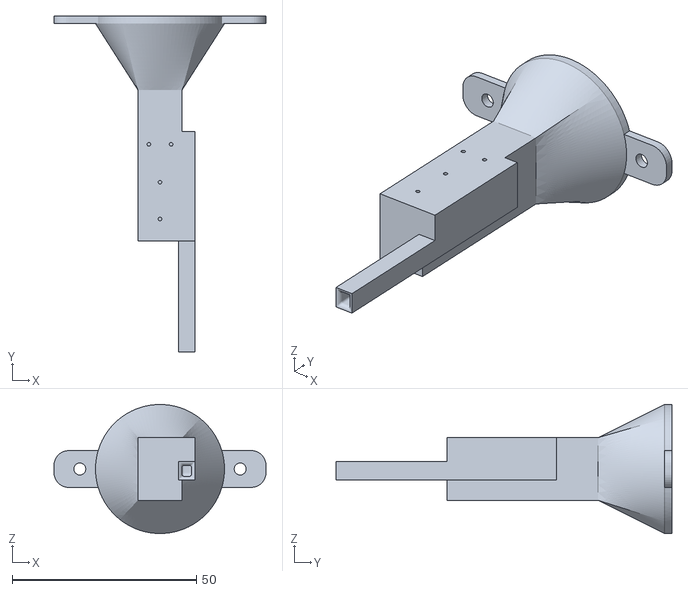
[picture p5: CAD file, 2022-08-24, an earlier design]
CAD/old/5ml_FunSiphon_2.5 rounded corner.stl
57.5 x 91.0 x 35.0

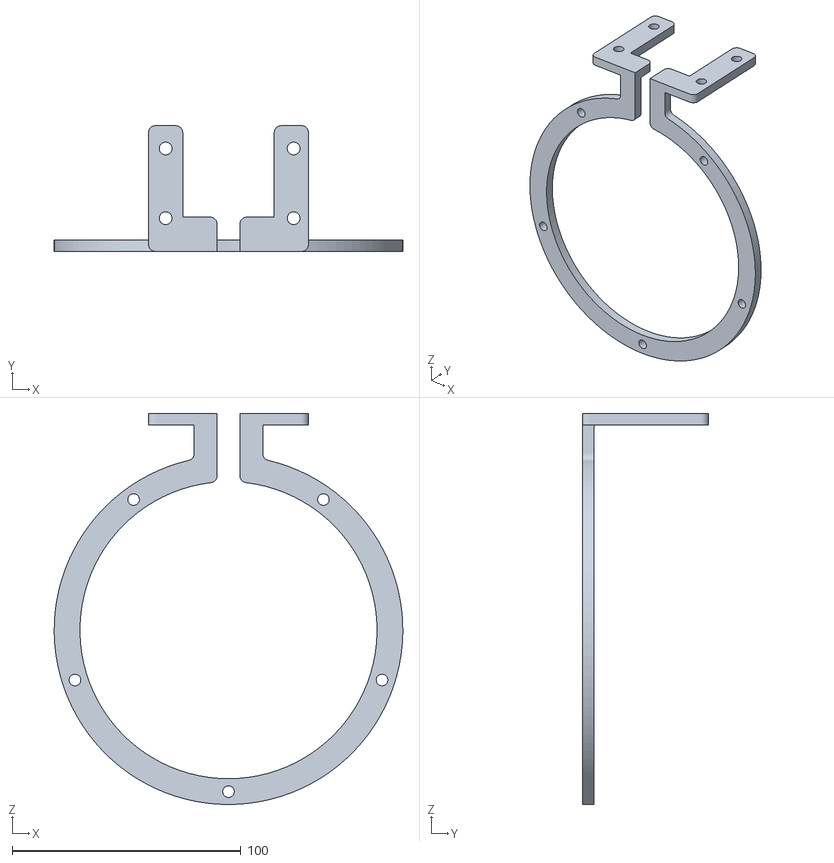
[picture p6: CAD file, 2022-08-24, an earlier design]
CAD/old/Vertical_Ring_Mount.stl
152.6 x 55.0 x 171.1

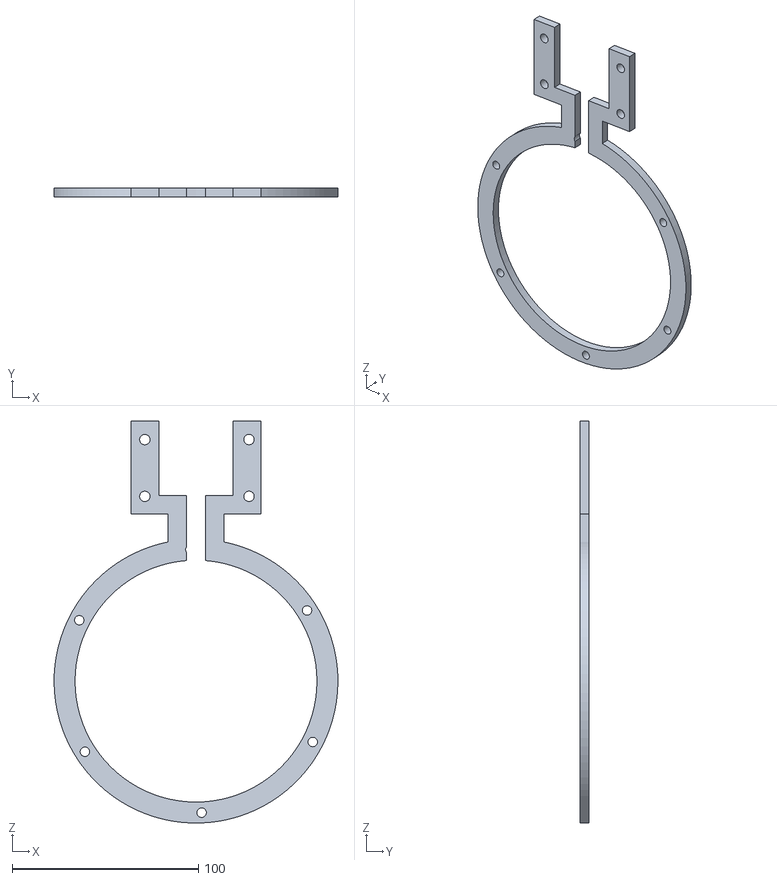
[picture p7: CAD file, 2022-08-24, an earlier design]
CAD/old/RingMount.stl
152.6 x 5.00 x 216.1

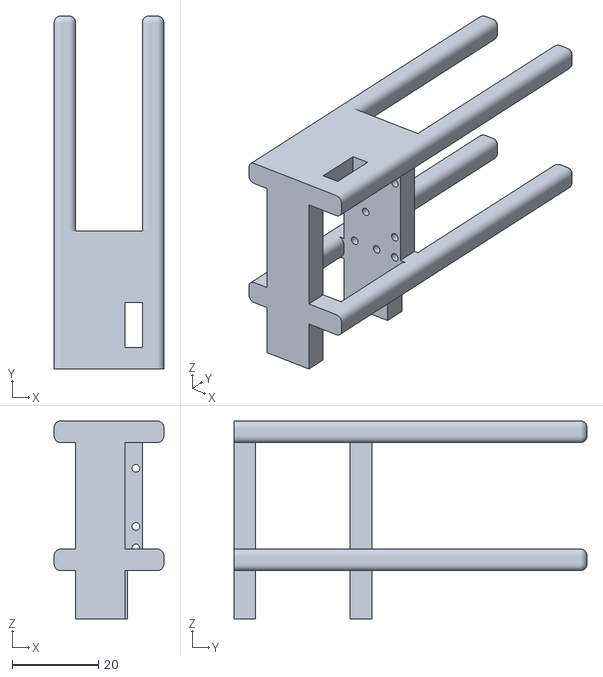
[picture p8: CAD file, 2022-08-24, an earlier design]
CAD/old/Wire_epoxy_platform.stl
25.5 x 82.0 x 46.0

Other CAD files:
CAD/old/5ml_FunSiphon_2.stl

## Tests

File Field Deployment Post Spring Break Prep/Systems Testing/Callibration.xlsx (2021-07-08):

 | Callibration
 | Using Deployment Code for System 1
 | Tuning at: 32
Samples | DI Water | 84 uS/cm | 100 uS/cm |  | UNDERTUNED
1 | 3402 | 8563 | 5674 | 6086
2 | 3335 | 8546 | 5679 | 6086
3 | 3391 | 8644 | 5460 | 6086
4 | 3388 | 8658 | 5773 | 6086
 |  | 5454
 |  | 5444
 |  | 5633
 |  | 5650
 | Callibration
 | Using Deployment Code for System 1
 | Tuning at: 80
Samples | DI Water | 84 uS/cm | 100 uS/cm
1 | 3987 | 11144 | 12964
2 | 4065 | 11402 | 12773
3 | 4142 | 11447 | 12892
4 | 4196 | 11404 | 12873

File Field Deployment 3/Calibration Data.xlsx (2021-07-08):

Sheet: System 1
Tuned: | 63
 | 100 uS/cm | DI | Empty
 | 12280 | 3047 | 2668
Int Meas. | 100 | DI | Empty?
 | 11700 | 2799

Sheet: System 2
Tuned: | 63
 | 100 uS/cm | DI | Empty
 | 10293 | 2995 | 2863
Int Meas. | 100 | DI | Empty?
 | 10300 | 3576

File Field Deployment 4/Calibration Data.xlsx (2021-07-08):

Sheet: System 1
Trials | Open | DI Water | 23 | 84
1 | 2840 | 3777 | 4170 | 8523
2 | 2840 | 4040 | 4171 | 8550
3 | 2840 | 3336 | 4191 | 8739
4 | 2840 | 3306 | 4194 | 8729
5 | 2840 | 3301 | 4192 | 8715
 | 2840 | 3552 | 4183.6 | 8651.2

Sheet: System 2
Tuned: | 63
 | 100 uS/cm | DI | Empty
 | 10293 | 2995 | 2863
Int Meas. | 100 | DI | Empty?
 | 10300 | 3576

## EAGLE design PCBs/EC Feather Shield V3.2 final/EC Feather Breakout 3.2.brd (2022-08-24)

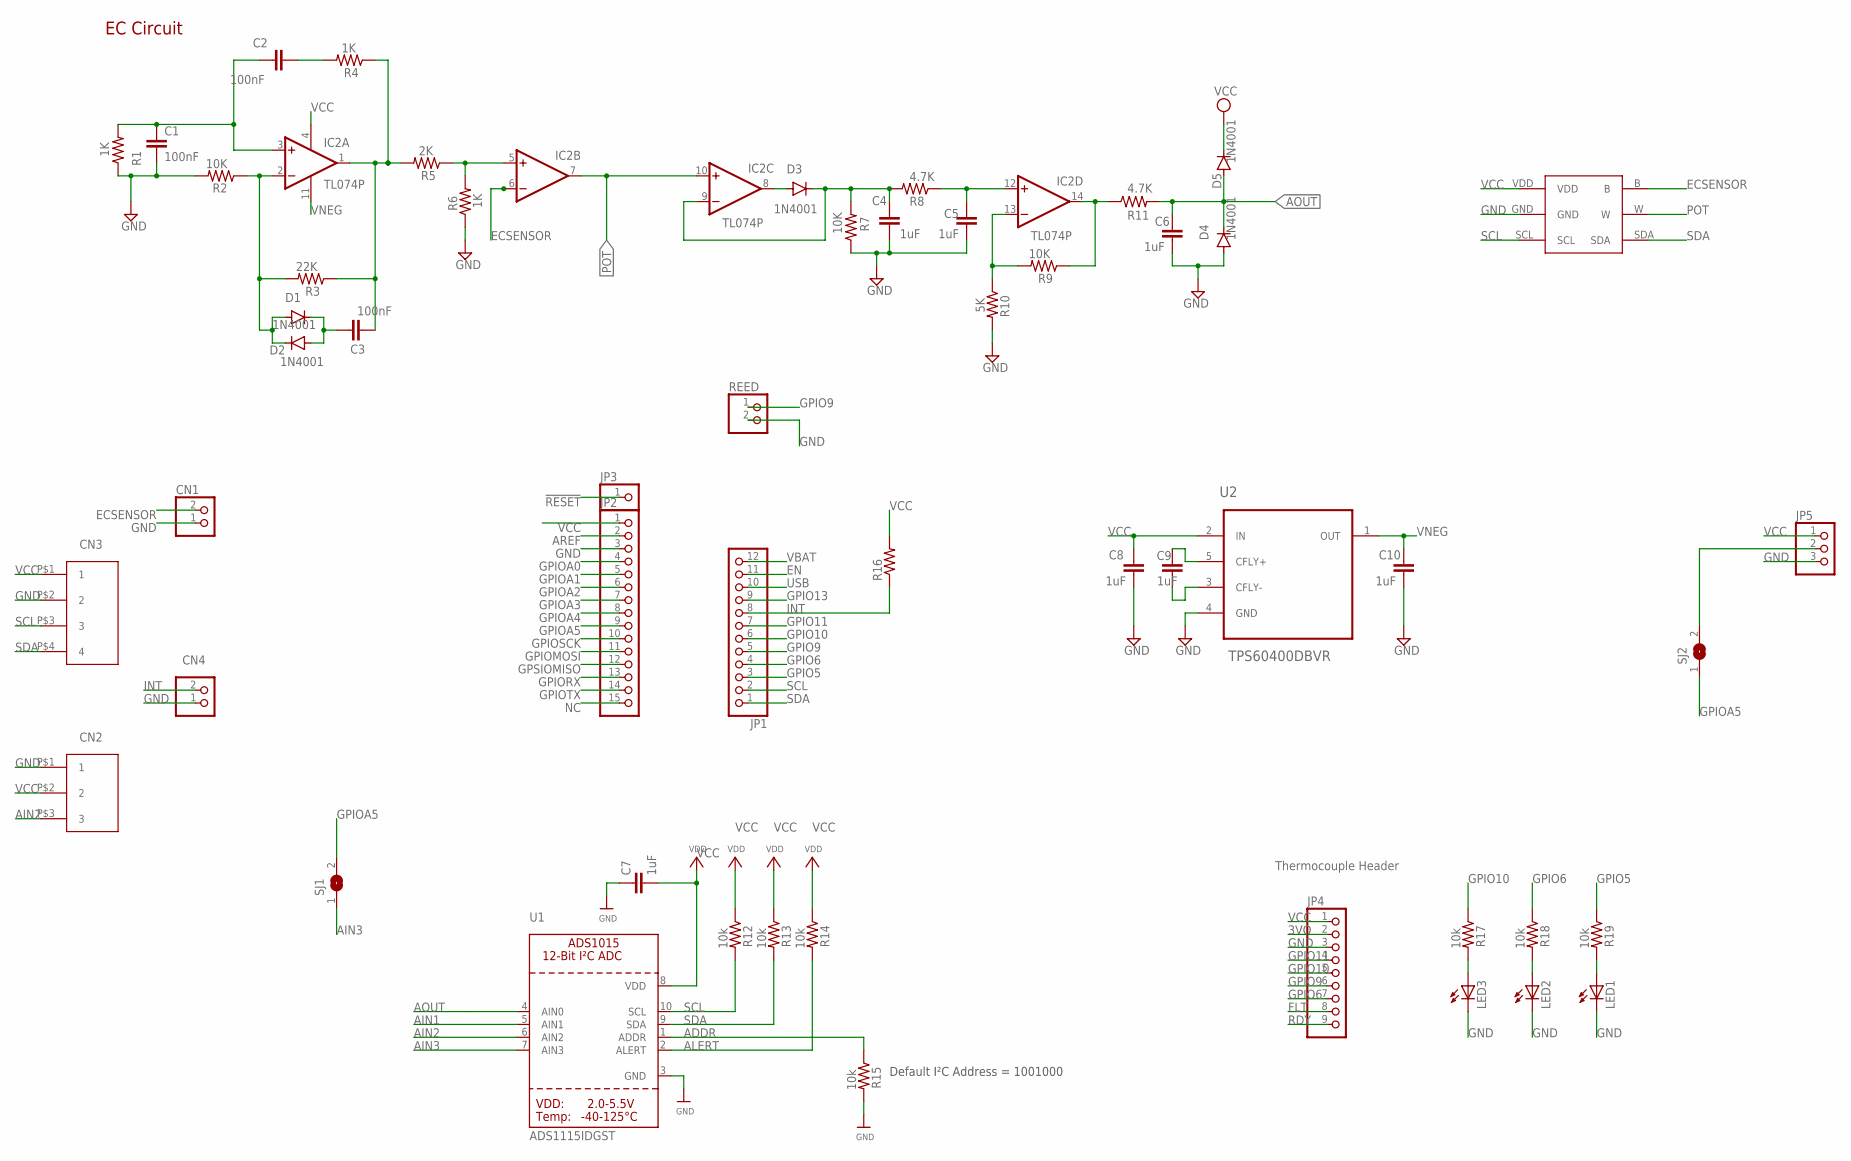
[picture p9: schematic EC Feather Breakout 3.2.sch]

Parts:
C1, C2, C3: 100nF; C1206
C4, C5, C6, C7, C8, C9, C10: 1uF; C1206
CN1, CN4: JST_2PIN-THM; JST-PH-2-THM
D1, D2, D3, D4, D5: 1N4001; D-5
IC2: TL074P; DIL14
JP1: PINHD-1X12-CB; 1X12-CB
JP2: PINHD-1X15-CB; 1X15-CB
JP3: PINHD-1X1CB; 1X01-CLEANBIG
JP4: PINHD-1X9; 1X09
JP5: PINHD-1X3CB; 1X03-CLEANBIG
LED1, LED2, LED3: LEDSMT1206; 1206
R1, R4, R6: 1K; R1206
R2, R7, R9: 10K; R1206
R3: 22K; R1206
R5: 2K; R1206
R8, R11: 4.7K; R1206
R10: 5K; R1206
R12, R13, R14, R15, R17, R18, R19: 10k; R1206
R16: R-US_M1206; M1206
REED: PINHD-1X2; 1X02
SJ1, SJ2: SJ
U1: ADS1115IDGST; MSOP10
U2: TPS60400DBVR; SOT95P280X145-5N
U$1: AD5246
U$7: JST_4PIN_2MM
U$9: JST_3PIN_2MM

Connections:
3VO: JP4.2
!RESET: JP3.1
ADDR: R15.1, U1.1 (ADDR)
AIN1: U1.5 (AIN1)
AIN2: U1.6 (AIN2), U$9.P$3 (3)
AIN3: SJ1.1, U1.7 (AIN3)
ALERT: R14.2, U1.2 (ALERT)
AOUT: C6.2, D4.C, D5.A, R11.2, U1.4 (AIN0)
AREF: JP2.2
ECSENSOR: CN1.2 (1), IC2.6 (-IN), U$1.B
EN: JP1.11
FLT: JP4.8
GND: C1.2, C4.1, C5.1, C6.1, C7.1, C8.1, C10.1, CN1.1 (2), CN4.1 (2), D4.A, JP2.3, JP4.3, JP5.3, LED1.C, LED2.C, LED3.C, R1.1, R2.2, R6.1, R7.1, R10.2, R15.2, REED.2, U1.3 (GND), U2.4 (GND), U$1.GND, U$7.P$2 (2), U$9.P$1 (1)
GPIO5: JP1.3, R19.1
GPIO6: JP1.4, JP4.7, R18.1
GPIO9: JP1.5, JP4.6, REED.1
GPIO10: JP1.6, JP4.5, R17.1
GPIO11: JP1.7, JP4.4
GPIO13: JP1.9
GPIOA0: JP2.4
GPIOA1: JP2.5
GPIOA2: JP2.6
GPIOA3: JP2.7
GPIOA4: JP2.8
GPIOA5: JP2.9, SJ1.2, SJ2.1
GPIOMOSI: JP2.11
GPIORX: JP2.13
GPIOSCK: JP2.10
GPIOTX: JP2.14
GPSIOMISO: JP2.12
INT: CN4.2 (1), JP1.8, R16.1
unnamed: C1.1, C2.1, IC2.3 (+IN), R1.2
unnamed: C2.2, R4.2
unnamed: C3.2, IC2.1 (OUT), R3.1, R4.1, R5.2
unnamed: D1.A, D2.C, IC2.2 (-IN), R2.1, R3.2
unnamed: IC2.5 (+IN), R5.1, R6.2
unnamed: JP5.2, SJ2.2
unnamed: C3.1, D1.C, D2.A
unnamed: C4.2, D3.C, IC2.9 (-IN), R7.2, R8.2
unnamed: D3.A, IC2.8 (OUT)
unnamed: C5.2, IC2.12 (+IN), R8.1
unnamed: IC2.13 (-IN), R9.2, R10.1
unnamed: IC2.14 (OUT), R9.1, R11.1
unnamed: LED3.A, R17.2
unnamed: LED2.A, R18.2
unnamed: LED1.A, R19.2
unnamed: C9.2, U2.5 (CFLY+)
unnamed: C9.1, U2.3 (CFLY-)
NC: JP2.15
POT: IC2.7 (OUT), IC2.10 (+IN), U$1.W
RDY: JP4.9
SCL: JP1.2, R12.2, U1.10 (SCL), U$1.SCL, U$7.P$3 (3)
SDA: JP1.1, R13.2, U1.9 (SDA), U$1.SDA, U$7.P$4 (4)
USB: JP1.10
VBAT: JP1.12
VCC: C7.2, C8.2, D5.C, IC2.4 (V+), JP2.1, JP4.1, JP5.1, R12.1, R13.1, R14.1, R16.2, U1.8 (VDD), U2.2 (IN), U$1.VDD, U$7.P$1 (1), U$9.P$2 (2)
VNEG: C10.2, IC2.11 (V-), U2.1 (OUT)

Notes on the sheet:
EC Circuit
Default I²C Address = 1001000
CN4
CN2
CN3
Thermocouple Header

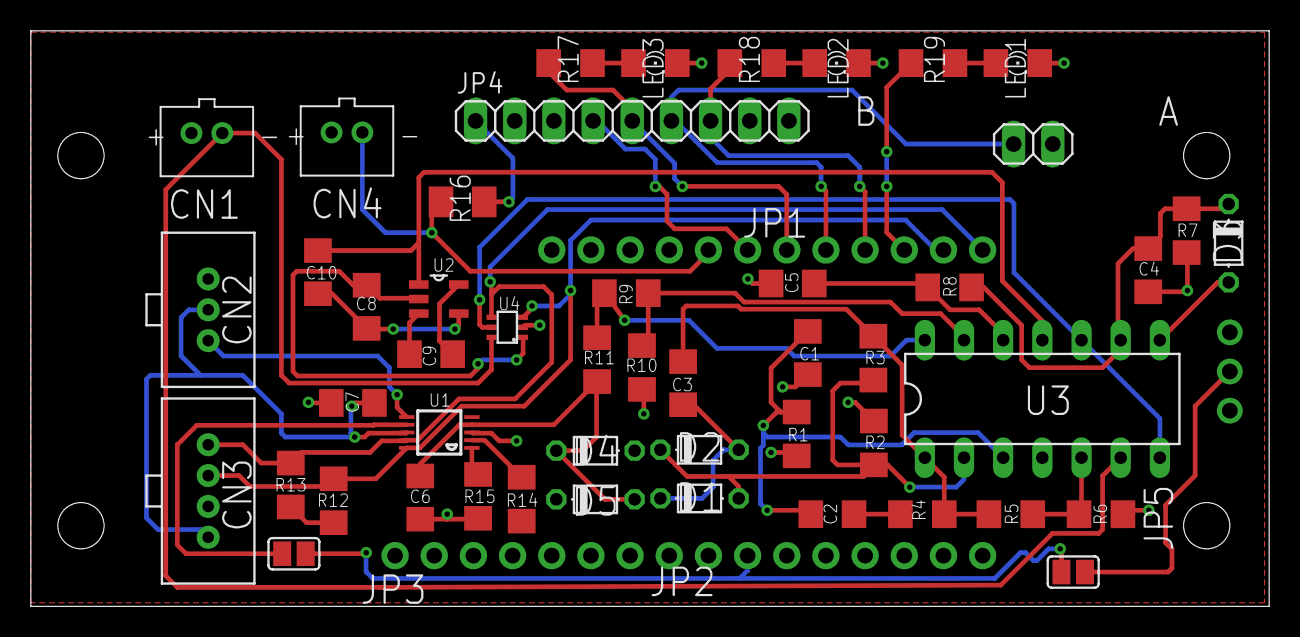
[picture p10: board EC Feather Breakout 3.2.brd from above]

Board: 2 copper layers, 80.3 x 37.3 mm, 53 parts (0 on the bottom side), 36 nets.

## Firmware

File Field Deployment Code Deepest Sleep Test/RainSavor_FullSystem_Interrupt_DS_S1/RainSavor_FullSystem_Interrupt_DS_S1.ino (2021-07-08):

/*
 * OPEnS Lab
 * Software for the RainSavor Project
 * Dr Chet Udell, Dr Segura
 * 
 * This software operates the electronics for the RainSavor project under the OPEnS lab at Oregon State University and is open source. All of the supporting files, such as electrical design, mechanical design, etc., 
 * are hosted on the OPEnS Lab wiki. 
 * The goal of this system is to sample rainfall in storms at installed locations. This software is the basis for data sampling. All of the sensing is done in hardware with a custom sensor, this software is 
 * peripheral to that sensor. This sketch will simply sample the voltages at the ADC and log it to an SD along with a timestamp. This sketch also utilizes a deep sleep mode to increase battery length
 * and field duration of the system. An interrupt system is used with the deep sleep to allow the controller to take a sample during rainfall events. 
 * 
 * This code heavily utilizes the OPEnS Loom library and software. It also assumes a OPEnS Hypnos board is being used for power control, RTC access, and SD logging. These must be present for correct operation. 
 * 
 */
  
 
//Initlialize libraries
#include <Loom.h>
#include <Wire.h>
#include <EnableInterrupt.h>


//Declare Constants & Variables
#define HYPNOS3 5
const byte VR_ADDR = 0x2E;  //I2C address for the AD5246 (variable resistor)
const byte VR_VAL = 20;

#define pin_select 12

int measure = 0;


//Initialize Loom dependencies
const char* json_config =
#include "config.h"
;

LoomFactory<
  Enable::Internet::Disabled,
  Enable::Sensors::Enabled,
  Enable::Radios::Disabled,
  Enable::Actuators::Disabled,
  Enable::Max::Disabled
>ModuleFactory{};

LoomManager Loom{ &ModuleFactory };

//Create the function that occurs when the interrupt triggers
void interruptFunction() {
  if (measure == 0)
  {
    LPrintln("\nButton Pressed Test");
    //Loom.measure();
    //Loom.package();
    measure = 1;
  }
}


//Custom function to communicate with I2C devices on the bus
void send_data(byte addr, byte data) {
  Wire.beginTransmission(addr);

  Wire.write(data);

  Wire.endTransmission(true);
}


//General Setup
void setup() {
  //Enable correct power rails from Hypnos
  pinMode(HYPNOS3, OUTPUT); //Don't worry about the 5V rail - not in use for this project
  digitalWrite(HYPNOS3, LOW);
  Wire.begin();
  
  
  //Begin serial communication as usual
  Loom.begin_serial(true);

  //Setup Loom
  Loom.parse_config(json_config);

  //Interrupt stuff
  pinMode(pin_select, INPUT_PULLUP);
  enableInterrupt(pin_select, interruptFunction, FALLING); //CHANGE works

  //Send data to AD5246 Variable Resistor
  send_data(VR_ADDR, VR_VAL);

  //LPrintln("\n** SETUP COMPLETE **");

}


void loop() {

  if (measure == 1)
  {
    //Turn on power
    digitalWrite(HYPNOS3, LOW); 
    pinMode(23, INPUT);
    pinMode(24, INPUT);
    pinMode(10, INPUT);
    Loom.power_up();
    
    delay(50);
    send_data(VR_ADDR, VR_VAL);
    //measure = 0;
    delay(50);//was 400
    Loom.record();
    Loom.display_data();
    //Loom.pause();
    Loom.SDCARD().log();
    delay(1000);
    measure = 0;
  }

  //Turn off power
  digitalWrite(HYPNOS3, HIGH);
  pinMode(23, INPUT);
  pinMode(24, INPUT);
  pinMode(10, INPUT);
  Loom.SleepManager().sleep();


}

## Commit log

2021-07-08 First commit. Adding all of Cameron's code
    [Calibration Data.xlsx, Callibration.xlsx]
2022-08-24 Re-organized, added 3d prints and pcbs
    [5ml_FunSiphon_2.5 rounded corner.stl, 5ml_FunSiphon_2.stl, BOM RainSavor.xlsx, Calibration Data.xlsx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]
2022-09-03 Resistor value setting moved to loop, print to sd
    Sleep resets to maximum value
2022-10-31 Added no interrupt code version
    Tracking interrupt wires through ADS1115 and taking data every 5 seconds.
2023-08-09 Updated design files
    [5ml_FunSiphon_2.5 rounded corner.stl, 5ml_FunSiphon_2.stl, RingMount.stl, Vertical_Ring_Mount.stl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]
